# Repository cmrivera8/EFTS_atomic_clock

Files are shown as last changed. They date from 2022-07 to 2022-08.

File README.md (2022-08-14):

# EFTS_atomic_clock
The atomic clock described in this repository is used in the yearly European Frequency and Time Seminar (EFTS) hosted at ENSMM. This repository contains the original design files as well as the improved control software GUI in python (EFTS_atomic_clock/mac_control_program/qt_mac.py) and the microcontroller code (EFTS_atomic_clock/mac/mac.ino) embedded in the demonstrator.

When I started my contribution on this project, there were three atomic clocks, out of which only one was working correctly. The other two were marginally operational, with a weak absorption signal and low signal-to-noise ratio. This made it very difficult to lock the servo loops on the desired electronic transition. Moreover, the GUI was not intuitive and resulted in a not-ideal learning experience for the seminar attendees.

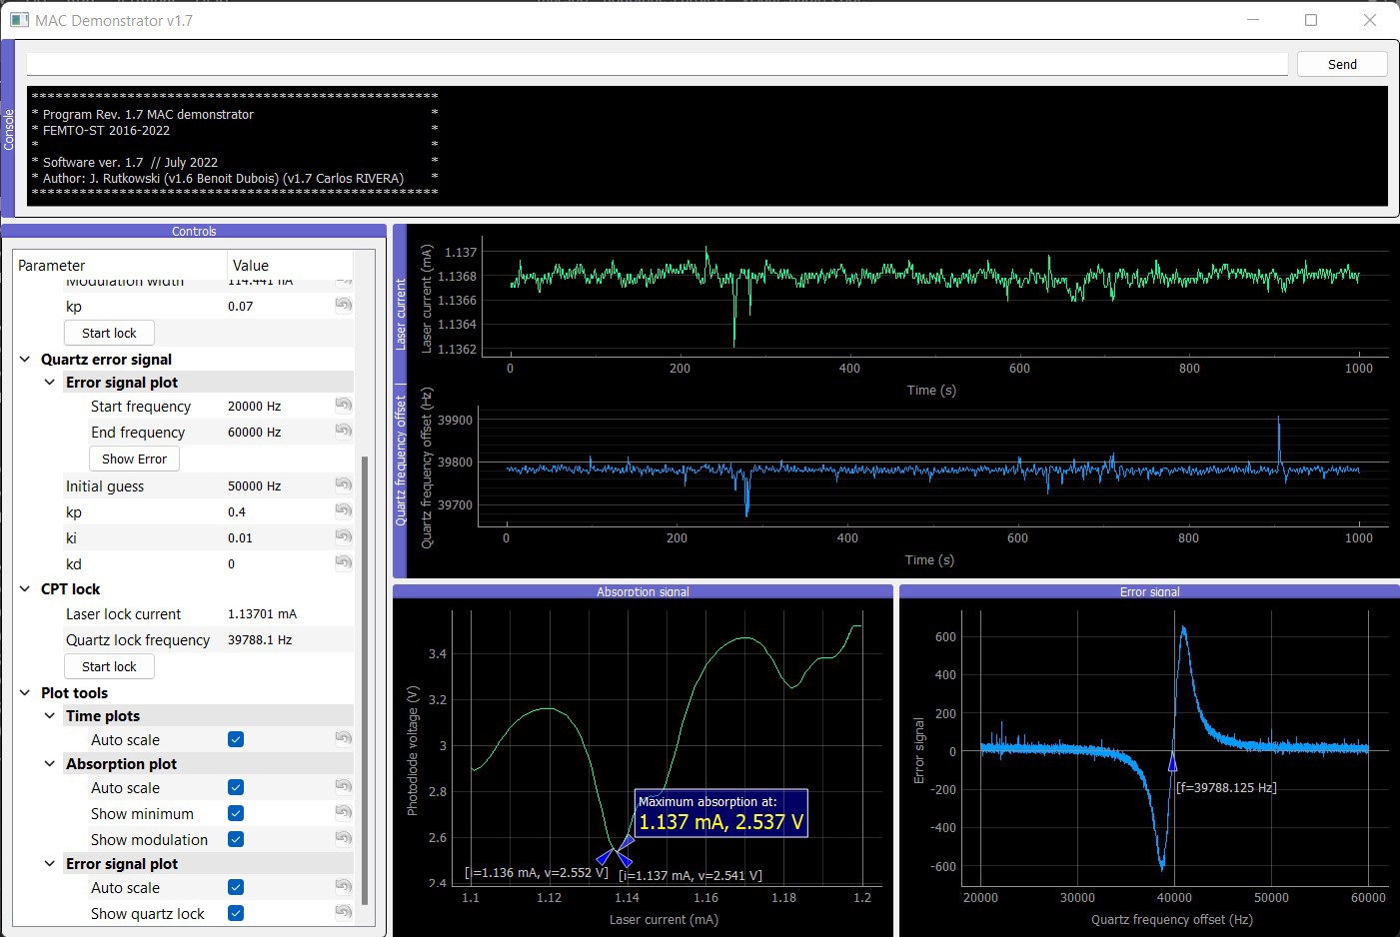
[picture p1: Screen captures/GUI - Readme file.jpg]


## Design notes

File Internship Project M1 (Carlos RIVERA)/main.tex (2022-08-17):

\documentclass[a4paper,12pt]{article}
\usepackage{geometry}
\geometry{a4paper} %paper format
\geometry{verbose,a4paper,tmargin=1.5cm,bmargin=2cm,lmargin=1.5cm,rmargin=1.5cm}  %margins

%\renewcommand{\thesection}{\Roman{section}}
%\renewcommand{\thesubsection}{\thesection.\Roman{subsection}}

\usepackage[english]{babel}
\usepackage{amsmath}
\usepackage{graphicx}
\usepackage{caption} %To use caption set up
\usepackage{subcaption}
\usepackage{wrapfig} %Wrap text to figure
\usepackage[export]{adjustbox} %Image aligment %Not compatible with \linespread
\usepackage{float}
\usepackage[singlespacing]{setspace}
\linespread{0.8}
\usepackage{hyperref}
\usepackage{titlesec}
\usepackage[T1]{fontenc}
%\usepackage{mathpazo} %Selecting font
\usepackage{microtype} %Improve justification
\usepackage{siunitx} %SI notation
%\usepackage[landscape]{geometry}
\usepackage{array}
\usepackage{color} %red, green, blue, yellow, cyan, magenta, black, white
\usepackage{bigdelim}
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
  morekeywords={scp,mkdir,rm,chmod,sudo,cp, apt, chown},              % Add keywords here
  commentstyle=\color{codegreen},
  keywordstyle=\bfseries\color{magenta},
  numberstyle=\tiny\color{codegray},
  stringstyle=\color{codepurple},
  breaklines=true,                % sets automatic line breaking
  tabsize=3,		              % sets default tabsize to 3 spaces
  frame=shadowbox,
  numbers=left,
  numberstyle=\scriptsize,
  prebreak=\usebox{\myprebreak},
  postbreak=\usebox{\mypostbreak},
  alsoletter=0123456789
}

\lstdefinestyle{c++}{
  language     = c++,
  basicstyle   = \footnotesize \ttfamily,
%   keywordstyle = [1]\color{keyword},
%   keywordstyle = [2]\color{STD},
%   keywordstyle = [3]\color{bits},
%   commentstyle = \color{comment},
%   stringstyle=\color{literals},
  morekeywords={self},              % Add keywords here
  commentstyle=\color{codegreen},
  keywordstyle=\color{magenta},
  numberstyle=\tiny\color{codegray},
  stringstyle=\color{codepurple},
  breaklines=true,                % sets automatic line breaking
  tabsize=3,		              % sets default tabsize to 3 spaces
  frame=shadowbox,
  numbers=left,
  numberstyle=\scriptsize,
  prebreak=\usebox{\myprebreak},
  postbreak=\usebox{\mypostbreak},
  alsoletter=0123456789
}
%

%Remove tab spaces
\newlength{\rawgobble}
\newlength{\gobble}
\newlength{\gobblea}
% The width of a single space. basicstyle from lstset should be used
\sbox0{\ttfamily \ }
% Remove a single space
\settowidth{\rawgobble}{\ttfamily \ }
\setlength{\rawgobble}{-\rawgobble}

\makeatletter
\def\sepstar#1*#2\relax{%
    \def\sepstarone{#1}%
    \def\sepstartwo{#2}%
}
\lst@Key{firstlineandnumber}\relax{\def\lst@firstline{#1\relax}\def\lst@firstnumber{#1\relax}}
\lst@Key{widthgobble}{0*0}{%
    % Reindent a bit by multiplying with 0.9, then multiply by tabsize and number of indentation levels
    \sepstar #1\relax
    \setlength{\gobble}{0.9\rawgobble}%
    \setlength{\gobble}{\sepstarone\gobble}%
    \setlength{\gobble}{\sepstartwo\gobble}%
    \setlength{\gobblea}{\gobble}%
    \addtolength{\gobblea}{10pt}%
    \def\lst@xleftmargin{\gobble}%
    \def\lst@framexleftmargin{\gobble}%
    \def\lst@numbersep{\gobblea}%
}
\makeatother
% Adding line number automatically
\makeatletter
\def\lst@MSkipToFirst{%
    \global\advance\lst@lineno\@ne
    \ifnum \lst@lineno=\lst@firstline
        \def\lst@next{\lst@LeaveMode \global\lst@newlines\z@
        \lst@OnceAtEOL \global\let\lst@OnceAtEOL\@empty
        \lst@InitLstNumber % Added to work with modified \lsthk@PreInit.
        \lsthk@InitVarsBOL
        \c@lstnumber=\numexpr-1+\lst@lineno % this enforces the displayed line numbers to always be the input line numbers
        \lst@BOLGobble}%
        \expandafter\lst@next
    \fi}
\makeatother
%
%Add extra level of sections
\usepackage{titlesec}
\usepackage{hyperref}

\titleclass{\subsubsubsection}{straight}[\subsection]

\newcounter{subsubsubsection}[subsubsection]
\renewcommand\thesubsubsubsection{\thesubsubsection.\arabic{subsubsubsection}}
\renewcommand\theparagraph{\thesubsubsubsection.\arabic{paragraph}} % optional; useful if paragraphs are to be numbered

\titleformat{\subsubsubsection}
  {\normalfont\normalsize\bfseries}{\thesubsubsubsection}{1em}{}
\titlespacing*{\subsubsubsection}
{0pt}{3.25ex plus 1ex minus .2ex}{1.5ex plus .2ex}

\makeatletter
\renewcommand\paragraph{\@startsection{paragraph}{5}{\z@}%
  {3.25ex \@plus1ex \@minus.2ex}%
  {-1em}%
  {\normalfont\normalsize\bfseries}}
\renewcommand\subparagraph{\@startsection{subparagraph}{6}{\parindent}%
  {3.25ex \@plus1ex \@minus .2ex}%
  {-1em}%
  {\normalfont\normalsize\bfseries}}
\def\toclevel@subsubsubsection{4}
\def\toclevel@paragraph{5}
\def\toclevel@paragraph{6}
\def\l@subsubsubsection{\@dottedtocline{4}{7em}{4em}}
\def\l@paragraph{\@dottedtocline{5}{10em}{5em}}
\def\l@subparagraph{\@dottedtocline{6}{14em}{6em}}
\makeatother

\setcounter{secnumdepth}{4}
\setcounter{tocdepth}{4}

% Add booktab table style:
\usepackage{booktabs}

\begin{document}

%% Title page
\begin{titlepage}

\newcommand{\HRule}{\rule{\linewidth}{0.5mm}}
\center 

\textsc{\LARGE Université Bourgogne Franche-Comté}\\[1.5cm] 
\textsc{\Large Internship Report Master 1}\\[0.5cm] 

\HRule \\[0.4cm]
{ \huge \bfseries Improvements on embedded systems used in the Time \& Frequencies Department}\\[0.4cm] %Improve title
\HRule \\[1.5cm]

\begin{figure}[!h]
\centering
\begin{subfigure}[b]{0.49\textwidth}
	\centering
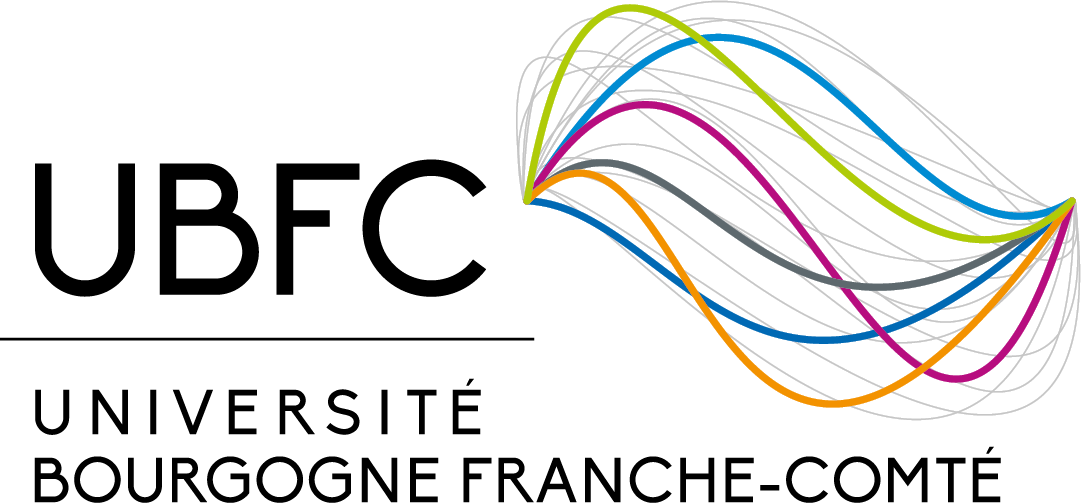
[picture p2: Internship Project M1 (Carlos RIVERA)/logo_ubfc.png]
	
	\captionsetup{justification=centering}
\end{subfigure}
\hfill
\begin{subfigure}[b]{0.49\textwidth}
	\centering
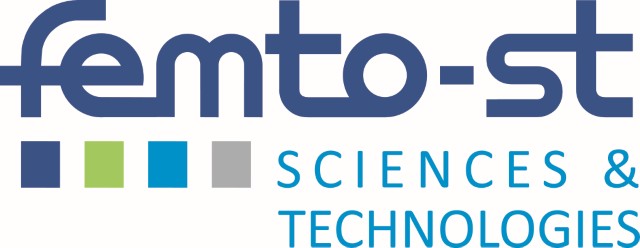
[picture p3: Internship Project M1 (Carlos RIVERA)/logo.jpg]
	
	\captionsetup{justification=centering}
\end{subfigure}
\end{figure}

\begin{center}
\vspace{2cm}
Presented by:\\ [0.4cm]
\begin{tabular}{ c    |    c } 
    Carlos RIVERA &  \normalsize \href{mailto:carlos_manuel.rivera_aguilar@edu.univ-fcomte.fr}{carlos\_manuel.rivera\_aguilar@edu.univ-fcomte.fr}
\end{tabular}
\end{center}
\vspace{2cm}
\begin{center}
Supervised by:\\ [0.4cm]
\begin{tabular}{ c    |    c } 
    Marion DELEHAYE &  \normalsize \href{mailto:marion.delehaye@femto-st.fr}{marion.delehaye@femto-st.fr} \\
    Rodolphe BOUDOT &  \normalsize \href{mailto:rodolphe.boudot@femto-st.fr}{rodolphe.boudot@femto-st.fr} \\
    Jean-Michel FRIEDT &  \normalsize \href{mailto:jeanmichel.friedt@femto-st.fr}{jeanmichel.friedt@femto-st.fr} \\
\end{tabular}
\end{center}
\vfill
{\large \today}\\[1cm] 
\vfill 

\end{titlepage}
  
%Table of contents and figures
\tableofcontents
\thispagestyle{empty}
\newpage
\listoffigures
\thispagestyle{empty}
\lstlistoflistings
\thispagestyle{empty}
\pagebreak

\setcounter{page}{1}

%Introduction:
\section{Introduction} 
The Time \& Frequencies department carries out investigations in applications and metrology of resonators and oscillators. The department is multifaceted with a focus on several scientific domains like electronics, hyperfrequency, acoustics, sciences and the shaping of crystalline materials, MEMS, photonics, signal processing, atomic physics, etc \cite{2022}.

The department’s research is conducted by three teams PiezoMEMS team, CoSyMA team (Composants et Systèmes Micro-Acoustiques) and OHMS team (Ondes, Horloges, Métrologie et Systèmes). The teams also work on common projects.

One of the domains on which OHMS team works is the creation of new frequency standard instruments (i.e. Atomic Clocks). The following technical report describes my collaboration with this department, specifically with OHMS team, as part of my internship for the Master 1 degree in Complex Systems, specialization: Smart Integrated Systems.

I worked on two separate projects; the first is "Superradiant laser instrumentation process", in which I improved the local network communication between the computers and the embedded system. The second project is "Improvements on CPT-based Cs microcell Atomic Clock pedagogical model" where I enhanced the performance and graphical user interface of the control software, and fixed two non-working atomic clocks (out of the existing three clocks).

%worked on 2 projects
%% First project
\section{Superradiant laser instrumentation process}
\subsection{Introduction}
The superradiant laboratory aims at generating an ultra-stable laser signal based on superradiant ytterbium atoms. Several lasers are used to achieve this. One of these lasers is at 399 nm (\mbox{751.3595 THz}) and it is used to excite the ytterbium atoms on an electronic transition that is 30 MHz wide. Hence, the laser frequency should be controlled within less than 30 MHz.

The laser frequency is measured within a few MHz using a Wavelength meter model WS8-2 manufactured by HighFinesse, that communicates, using UDP protocol, from a \textit{Windows computer} to a \textit{Red Pitaya} board (via Ethernet) to implement a PID control that regulates this frequency.

This communication process was dysfunctional, and it was not possible to re-use the UDP Server (\textit{Windows computer}) after the UDP Client (\textit{Red Pitaya}) was closed (and opened again to use a new setpoint frequency). It was necessary to open and close the UDP client twice to overcome this issue, which was very unreliable. A more robust protocol was intended, and I was able to modify both the Server and Client software to fix this problem.

Before the modifications took place, three computers were involved, hereafter referred to as:

\begin{itemize}
\itemsep 0em % To reduce space between items
    \item \textit{Windows computer:} this computer is running Windows 10 and had installed the wavelength meter software, UDP Server and the laser controller software. Since the first two do not require too much computational power and were malfunctioning when USB cameras used in the experiment were connected, a minimalistic single board computer, called \textit{LattePanda}, was later implemented (see section \ref{section:installation_lattepanda}).
    \item \textit{Artiq computer:} this computer is running Linux (Debian distribution) and is used to control the whole experiment via an Artiq\footnote{ARTIQ: Advanced Real-Time Infrastructure for Quantum physics is a control system for quantum information experiments, providing both hardware and software.} interface.
    \item \textit{Other computer:} located in another laboratory and running Linux, this computer contained the compilation toolchain for the \textit{Red Pitaya} board, as well as the UDP client software in charge of regulating the laser frequency, this computer was accessed and controlled remotely by the \textit{Artiq computer} via SSH\footnote{SSH: Secure Shell is a network communication protocol that enables two computers to communicate and share data.}.
\end{itemize}

% \subsection{Context} %Introduction and context are the same

Before I started my internship, the instrumentation scheme used to control the experiment's laser frequency is presented in figure \ref{fig:schematic}. A voltage controlled laser emits light and its frequency is then measured by a Wavelength meter. The instrument communicates the results to the \textit{Windows computer} via USB.

In the \textit{Windows computer}, the dedicated software of the instrument is installed. The results of the measurements are then streamed by a dedicated C++ program over Ethernet (UDP socket) to the \textit{Red Pitaya}.

The \textit{Red Pitaya} compares the measured value with a setpoint to generate an error signal that is then used to correct the laser frequency through a PID close loop controller.

The frequency setpoint is provided to the \textit{Red Pitaya} over Ethernet (SSH) by the \textit{Artiq computer} (Linux based), which allows having an interface with an option to modify the laser frequency and one to turn the laser lock on and off.

Another laboratory's computer (\textit{Other computer}, Linux based) was responsible to provide a NFS\footnote{NFS: Network File System is a networking protocol for distributed file sharing. A file system defines the way data in the form of files is stored and retrieved from storage devices, in our case from the computer to the \textit{Red Pitaya}.} directory to the \textit{Red Pitaya}. This allows to have real-time interaction with its content from the \textit{Artiq computer}. It also provides a cross-compilation toolchain, which is why multiple SSH processes were involved to modify the \textit{Red Pitaya} content (including the program written in C to voltage control the laser frequency).

\begin{figure}[!h]
    \centering
    
    \captionsetup{justification=centering}
    \caption{Laser frequency control instrumentation scheme at the beginning of the project.}
    \label{fig:schematic}
\end{figure}

For this project, the following objectives were set:
\begin{itemize}
\itemsep 0em % To reduce space between items
    \item To correct the fact that the cross compilation chain (oscimpDigital\footnote{oscimpDigital is an ecosystem designed to provide a consistent, chip independent, software/hardware cross-compile solution.} and Buildroot\footnote{Buildroot is a simple, efficient and easy-to-use tool to generate embedded Linux systems through cross-compilation.}) and the NFS directories were stored in \textit{Other laboratory's computer}, for which it was preferred to migrate them to the \textit{Artiq computer} (see section \ref{section:migration_section}).
    \item To have a standalone, single board computer running the Wavelength meter software and the C++ program, given that these two do not require a lot of computational power and that there are conflicts whenever a camera is connected via USB to the Windows Desktop computer (see section \ref{section:installation_windows10} and \ref{section:installation_lattepanda}).
    \item To fix the network communication software on the \textit{Red Pitaya} (written in C) and on the \textit{Windows computer} (written in C++), given that the communication between the two was not consistent, and it was necessary to close the socket twice whenever a new frequency setpoint was selected. Also, to implement a method that interrupts the communication process from the Artiq interface (see section \ref{subsec:udp_correction}).
    \item To have an automated start-up process to mount the NFS directory on the \textit{Red Pitaya} at power up, in case the latter had a power outage or just for a convenient everyday operation of the experiment (see section \ref{section:start_up_automation}).
\end{itemize}

\subsection{Migration of Red Pitaya environment between two computers}
\label{section:migration_section}

The migration process of the cross compilation chain (oscimpDigital and Buildroot) and the
NFS directory from the \textit{Other lab computer} to the \textit{Artiq computer} (as presented in figure \ref{fig:schematic}) is described in figure \ref{fig:migration_flowchart}.

\begin{figure}[!h]
    \centering
    
    \captionsetup{justification=centering}
    \caption{Migration process flowchart.}
    \label{fig:migration_flowchart}
\end{figure}

%Step 1:
\begin{step}
The folders "oscimpDigital" and "redpitaya" were copied from the \textit{Other computer} to the \textit{Artiq computer} using the "scp" command (listing \ref{lst:copy_osc_red}).

\begin{lstlisting}[style=bash,label={lst:copy_osc_red},caption={Copying files from the \textit{Other computer} to the \textit{Artiq computer}.}]
cd /home/manip/redpitaya/
scp -r pyb@172.16.120.154:~/oscimp/oscimpDigital ./oscimpDigital_pyb
scp -r pyb@172.16.120.154:~/oscimp/redpitaya ./redpitaya_pyb
\end{lstlisting}

\end{step}

%Step 2:
\begin{step}
It was necessary to download and install Buildroot in the \textit{Artiq computer}, it's imperative to download the new Buildroot files before the compilation instead of using the existing ones from the \textit{Other computer}, the latter contain hard links that are not compatible with the new location.

Running "make" using the old files may lead to unwanted results, such as the usage of the entire hard-disk. First the version "2019.05-rc3" was downloaded from \hyperlink{https://buildroot.org/downloads/buildroot-2019.05-rc3.tar.gz}{https://buildroot.org/downloads/buildroot-2019.05-rc3.tar.gz} and then extracted (listing \ref{lst:unpack_buildroot}), the name of the resulting folder was changed from "buildroot-2019.05-rc3" to "buildroot-2019.05-rc3\_redpitaya\_pyb".

\begin{lstlisting}[style=bash,label={lst:unpack_buildroot},caption={Extracting Buildroot.}]
tar -xf buildroot-2019.05-rc3.tar.gz
rm buildroot-2019.05-rc3.tar.gz
\end{lstlisting}

\end{step}

%Step 3:
\begin{step}
As per trabucayre's "redpitaya" GitHub repository \cite{trabucayre}, we must set up the "BR2\_EXTERNAL" variable to the location where the "redpitaya" directory is, as show in listing \ref{lst:br2_external}, to provide Buildroot based support for Red Pitaya (12, 14, and 16 bits) board.

\begin{lstlisting}[style=bash,label={lst:br2_external},caption={Setting the BR2\_EXTERNAL variable.}]
export BR2_EXTERNAL=~/redpitaya/redpitaya_pyb/
\end{lstlisting}

\end{step}

%Step 4:
\begin{step}
In order to match the previous installation, the board configuration file (options and features selected for the resulting OS) was copied into the \textit{Artiq computer} and then compiled with the "make" command, the commands of listing \ref{lst:copy_config} were performed in the directory "/home/manip/redpitaya/buildroot-2019.05-rc3\_redpitaya\_pyb/".

\begin{lstlisting}[style=bash,label={lst:copy_config},caption={Copying board ".config" file to the new Buildroot directory.}]
scp pyb@172.16.120.154:~/oscimp/redpitaya_buildroot/.config ./
make
\end{lstlisting}

In the middle of the compilation, there was an error fetching the file "linux-xilinx-v2019.1.tar.gz" from the internet, which is why it was copied from the \textit{Other computer} directly (listing \ref{lst:linux-xilinx}).

\begin{lstlisting}[style=bash,label={lst:linux-xilinx},caption={Copying xilinx file from previous installation.}]
scp pyb@172.16.120.154:~/oscimp/redpitaya_buildroot/dl/linux/linux-xilinx-v2019.1.tar.gz ./linux/linux-xilinx-v2019.1.tar.gz
make
\end{lstlisting}

\end{step}

%Step 5:
\begin{step}
Once the cross-compilation toolchain was installed, the next step was to set up the NFS directory in the \textit{Artiq computer}, following the instructions of oscimp's GitHub repository "oscimpDigital" \cite{oscimp}, the designated location was "/home/manip/redpitaya/oscimpDigital\_pyb/nfs" (listing \ref{lst:mkdir_nfs}).

\begin{lstlisting}[style=bash,label={lst:mkdir_nfs},caption={Creating NFS directory.}]
mkdir /home/manip/redpitaya/oscimpDigital_pyb/nfs
\end{lstlisting}

Inside the directory "/home/manip/redpitaya/oscimpDigital\_pyb/" the "settings.sh" file was found, which contains all environment variable information required for the compilation of the library, drivers and modules, as shown in listing \ref{lst:nfs_settings}, only the "BR\_DIR" and "OSCIMP\_DIGITAL\_NFS" variables needed to be updated.

\begin{lstlisting}[style=bash,label={lst:nfs_settings},caption={Updating variables "settings.sh" file.}]
export BR_DIR='/home/manip/redpitaya/buildroot-2019.05-rc3_redpitaya_pyb'
export OSCIMP_DIGITAL_NFS='/home/manip/redpitaya/oscimpDigital_pyb/nfs'
\end{lstlisting}

\end{step}

%Step 6:
\begin{step}
The libraries (listing \ref{lst:libraries}), drivers (listing \ref{lst:drivers}) and modules (listing \ref{lst:modules}) must be compiled; however, for the latter, the Makefile fails at copying the file "module\_generator" to the "/usr/local/bin" directory, thus, this was done manually with the \textbf{sudo} command (listing \ref{lst:modules}, line 5).

\begin{lstlisting}[style=bash,label={lst:libraries},caption={Compiling the libraries.}]
cd /home/manip/redpitaya/oscimpDigital_pyb/lib
make install_ssh
\end{lstlisting}

\begin{lstlisting}[style=bash,label={lst:drivers},caption={Installing the drivers.}]
export PATH=~/redpitaya/buildroot-2019.05-rc3_redpitaya_pyb/output/host/usr/bin/:$PATH
cd /home/manip/redpitaya/oscimpDigital_pyb/linux_driver
make install_nfsdir
\end{lstlisting}

\begin{lstlisting}[style=bash,label={lst:modules},caption={Compiling the module generator tool.}]
cd /home/manip/redpitaya/oscimpDigital_pyb/app/tools/module_generator
chmod +x Makefile
make install

sudo cp module_generator /usr/local/bin
\end{lstlisting}

\end{step}

\begin{step}
To finish the configuration on the new host (\textit{Artiq computer}), the "nfs-kernel-server" must be installed and the rights of the nfs directory changed, which allowed to have access to bistreams, applications and drivers through the NFS shared directory, this is accomplished by running the commands in listing \ref{lst:nfs_kernel}. 

\begin{lstlisting}[style=bash,label={lst:nfs_kernel},caption={Installing nfs-kernel server and changing directory rigths.}]
apt install nfs-kernel-server nfs-common

cd /home/manip/redpitaya/oscimpDigital_pyb/nfs
chown -R $(id -u).$(id -g) .
\end{lstlisting}

\end{step}

\begin{step}
The last step of the migration process was to compile and test the project (UDP Client on Red Pitaya), for which the project files were copied from the \textit{Other computer} and then compiled (listing \ref{lst:compile_test_1}).

%Check if this is the correct location line 3 and 4
\begin{lstlisting}[style=bash,label={lst:compile_test_1},caption={Copying project files and compile.}]
cd ~/redpitaya/oscimpDigital_pyb/projects/
scp -r pyb@172.16.120.154:~/oscimp/projects ~/redpitaya/oscimpDigital_pyb/projects/
make && make install

cd ~/redpitaya/oscimpDigital_pyb/nfs/redpitaya/laser_lock_LSR/bin/
scp -r pyb@172.16.120.154:~/oscimp/nfs/redpitaya/laser_lock_LSR/bin/start_lock.sh ./
scp -r pyb@172.16.120.154:~/oscimp/nfs/redpitaya/laser_lock_LSR/bin/laser_lock_LSR_us.sh ./
\end{lstlisting}

Running the software gave a segmentation fault error, upon close examination, it was not able to create and access a file in the current directory due to missing rights (fixed in listing \ref{lst:compile_test_2} line 1), there was also a missing file on the project's bitstreams directory (fixed in listing \ref{lst:compile_test_2} line 3 to 4).

\begin{lstlisting}[style=bash,label={lst:compile_test_2},caption={Correcting directory rights and copying missing file on bitstreams.}]
chmod -R 777 ~/redpitaya/oscimpDigital_pyb/nfs/redpitaya

cd ~/redpitaya/oscimpDigital_pyb/projects/laser_lock_LSR/design
cp laser_lock_LSR_wrapper.bit.bin ~/redpitaya/oscimpDigital_pyb/nfs/redpitaya/laser_lock_LSR/bitstreams/
\end{lstlisting}

\textbf{Conclusion:} Finally, the Red Pitaya software was tested successfully and there is no longer a dependency on the \textit{Other computer}. The new instrumentation scheme, as shown in figure \ref{fig:schematic_2}, requires only two computers located in the experiment's laboratory.

\begin{figure}[!h]
    \centering
    
    \captionsetup{justification=centering}
    \caption{Laser frequency control instrumentation scheme after migration.}
    \label{fig:schematic_2}
\end{figure}

\end{step}

\subsection{Installation of Windows 10 on Raspberry Pi}
\label{section:installation_windows10}
%introduction: we had an issue because there are some error when we want to use the wavelength meter software together with a camera on windows computer#1. This is because of the wavelength meter (the manufacturer admitted it). We decided to move the wavelength meter to a minimalistic computer.
While trying to use simultaneously the wavelength meter and some USB camera, we had multiple crashes on the Windows computer. It turns out that the wavelength meter software is defective and is not compatible with the use of some cameras simultaneously. We decided to install the wavelength meter software on a different computer. In a first instance, the option to have the Wavelength meter software on a single board Raspberry Pi computer was explored, for which there were two options:

\begin{itemize}
\itemsep 0em % To reduce space between items
\item To install a precompiled Raspbian OS\footnote{OS: Operating System} and emulate a Windows environment (using Wine\footnote{Wine is a free and open-source compatibility layer that aims to allow application software and computer games developed for Microsoft Windows to run on Unix-like operating systems.}) in order to install and run the software. In case of success, to tailor an optimized Linux operating system with Buildroot.
\item To install a ARM Windows 10 OS.
\end{itemize}

\subsubsection{Installation of Raspbian OS and Wine32 on the Raspberry Pi}

One of the main challenges for this approach is the fact that the Raspberry Pi ARM-based processor is fundamentally different from the x86-based CPU found in a typical PC. It was necessary to install box86 to emulate a x86 system on the Raspberry Pi and then Wine 32 to run Windows applications. However, incompatibility issues were found.\\

Despite of the fact that it was possible to install the software with wine32, it was not possible to obtain a correct behavior from the GUI of the software, it presented black sections and it was unresponsive as show in figure \ref{fig:raspbian}. 

\begin{figure}[!h]
    \centering
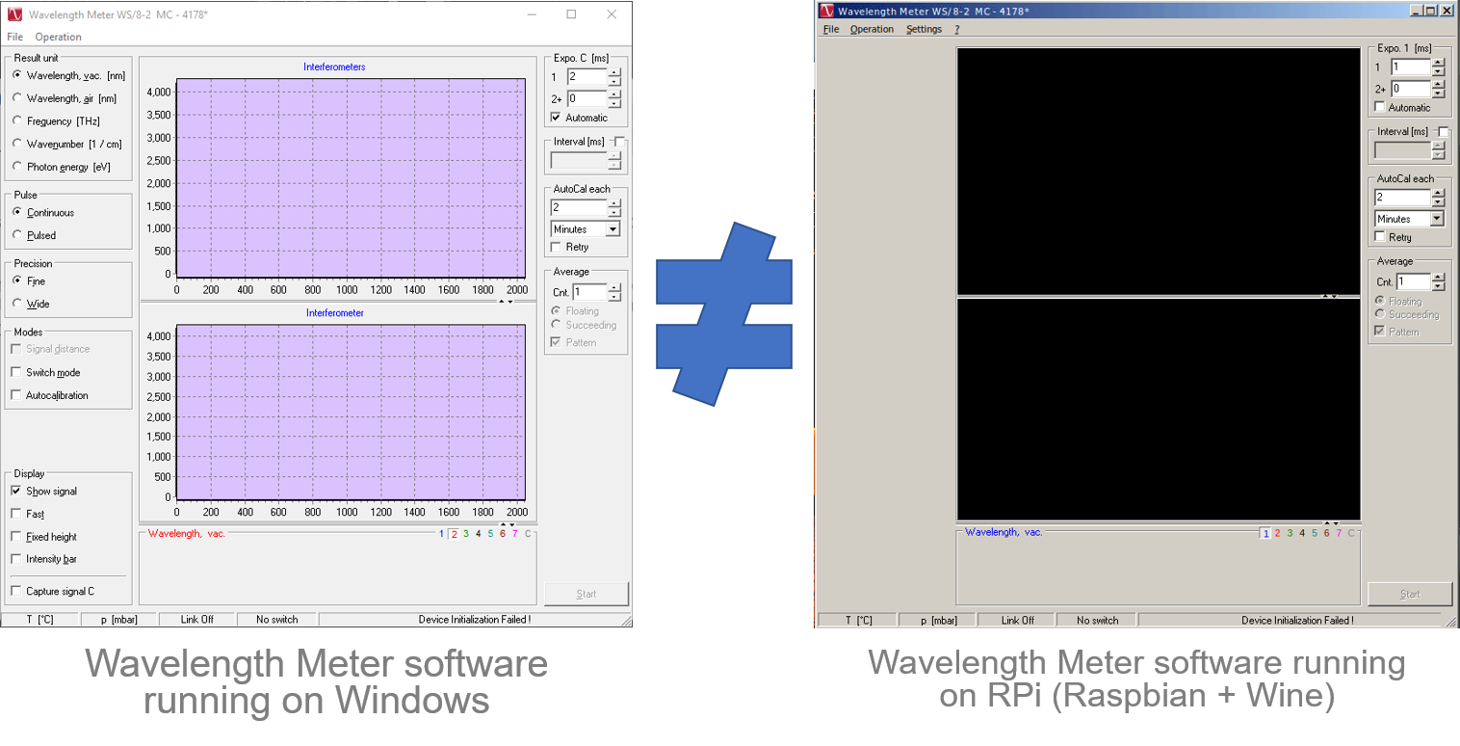
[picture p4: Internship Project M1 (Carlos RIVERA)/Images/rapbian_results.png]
    
    \captionsetup{justification=centering}
    \caption{Results of installing the wavelength meter software on Raspbian.}
    \label{fig:raspbian}
\end{figure}

\subsubsection{Installation of ARM Windows 10 OS on the Raspberry Pi}

Since it was not possible to run the Wavelength meter software on Raspbian due to their architectures incompatibility, the next option was to install a Windows 10 ARM version, which is compatible with the Raspberry Pi 4 and allows to run native Windows applications, it developed by the WoR (Windows on Raspberry Pi) project.

There is no legal way to download ISO files for Windows 10 ARM. Instead, a legal UUP dump file was downloaded, or "Unified Update Platform". This is a way for Microsoft to share its latest advances within its "Insider Preview" program. In short, the process was to download the UUP file, build a full ISO image from that file on the computer, then flash that ISO to boot on the Raspberry Pi.

With this approach it was possible to install the software on the Raspberry Pi. However, at initialization the device was not found (figure \ref{fig:device_not_found}), even though at installation a driver was installed. This appears to be an issue with the operating system which doesn't provide yet full support for peripherals such as USB ports. 

\begin{figure}[!h]
    \centering
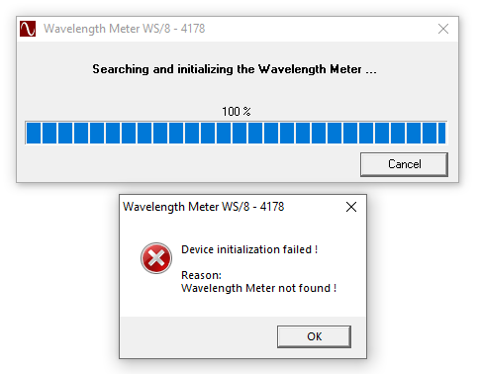
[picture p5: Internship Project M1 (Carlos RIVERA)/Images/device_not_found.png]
    
    \captionsetup{justification=centering}
    \caption{ARM Windows on RPi error: Wavelenth Meter not found.}
    \label{fig:device_not_found}
\end{figure}

\textbf{Conclusion:} The Raspberry Pi with ARM Windows was not robust enough to accommodate the software and be reliable in a daily basis operation, due to its slow speed and being prone to freeze or reset.

\subsection{Installation of Wavelength meter on Latte Panda single board computer}
\label{section:installation_lattepanda}

Finally, it was decided to install the Wavelength meter software on a Latte Panda single board computer (figure \ref{fig:latte_panda}) with the specifications described in table \ref{table:latte_panda_specs}.

\renewcommand{\arraystretch}{1.1}

\begin{table}[!h]
\begin{tabular}{ | l | l | }
\hline
\textbf{Processor}          & Intel Cherry Trail Z8350 Quad Core, 2M Cache, up to 1.92 GHz  \\ \hline
\textbf{Operating system}   & Pre-installed Windows 10                                      \\ \hline
\textbf{Ram}                & 4GB DDR3L                                                     \\ \hline
\textbf{Storage Capability} & 64GB                                                          \\ \hline
\textbf{GPU}                & Intel HD Graphics, 12 EUs @200-500 Mhz, single-channel memory \\ \hline
\textbf{Connectivity}       & WiFi and Bluetooth 4.0                                        \\ \hline
\textbf{Peripherals}        & One USB 3.0 port and two USB 2.0 ports                         \\ \hline
\textbf{Dimension of board} & 88 mm * 70 mm                                                    \\ \hline
\end{tabular}
\caption{Specifications of LattePanda 4G/64G.}
\label{table:latte_panda_specs}
\end{table}

\begin{figure}[!h]
    \centering
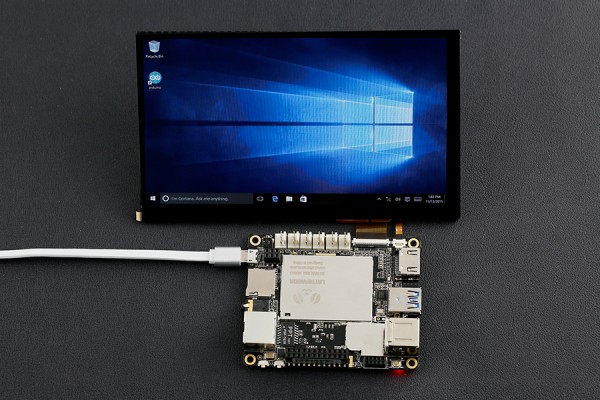
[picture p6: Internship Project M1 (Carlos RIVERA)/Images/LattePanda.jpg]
    
    \captionsetup{justification=centering}
    \caption{LattePanda single board computer running a full version of Windows 10.}
    \label{fig:latte_panda}
\end{figure}

\textbf{Conclusion:} The installation was flawless for both the Wavelength meter software as well as the UDP Server. After testing, it was possible to establish a connection from the LattePanda UDP Server to the Red Pitaya UDP Client, thus control the laser frequency from the Artiq interface. The resulting instrumentation scheme is presented in figure \ref{fig:schematic_3}.
%old: when the UDP socket must be closed by the Red Pitaya (see section \ref{subsec:udp_correction})

%Add screenshots/photos of the software working on the LattePanda.
% \textcolor{red}{Photos pending}

\begin{figure}[!h]
    \centering
    
    \captionsetup{justification=centering}
    \caption{Laser frequency control instrumentation scheme after the addition of LattePanda.}
    \label{fig:schematic_3}
\end{figure}

\newpage
\subsection{Correction of network communication between Red Pitaya and Wavelength meter}
\label{subsec:udp_correction}

The frequency measured by the wavelength meter is sent to the \textit{Red Pitaya} so that it can generate an error signal. Since the wavelength meter software comes with C++ libraries, it was chosen to use a UDP protocol to exchange information between the \textit{Windows computer} (running the wavelength meter software) and the \textit{Red Pitaya}.

An UDP datagram-based protocol was implemented before I started the internship. However this process was erratic and required the client socket (Red Pitaya) to be closed twice every time a new setpoint was selected. To circumvent this problem, a series of scripts were created and run from the \textit{Artiq computer} (SSH control of the Red Pitaya) but it was intended to have a robust and reliable network communication for the experiment that would also allow future enhancements to the instrumentation scheme.

\textit{Normally in the UDP protocol, the client does not form a connection with the server like in TCP and instead just sends a datagram to request for data. Similarly, the server doesn't need to accept a connection and just waits for datagrams request to arrive} \cite{geeksforgeeks_2022}, as show in figure \ref{fig:server-and-client}. However, upon closer inspection of the server and client code, the flowchart of figure \ref{fig:udp_before} was deduced.

\begin{figure}[!h]
    \centering
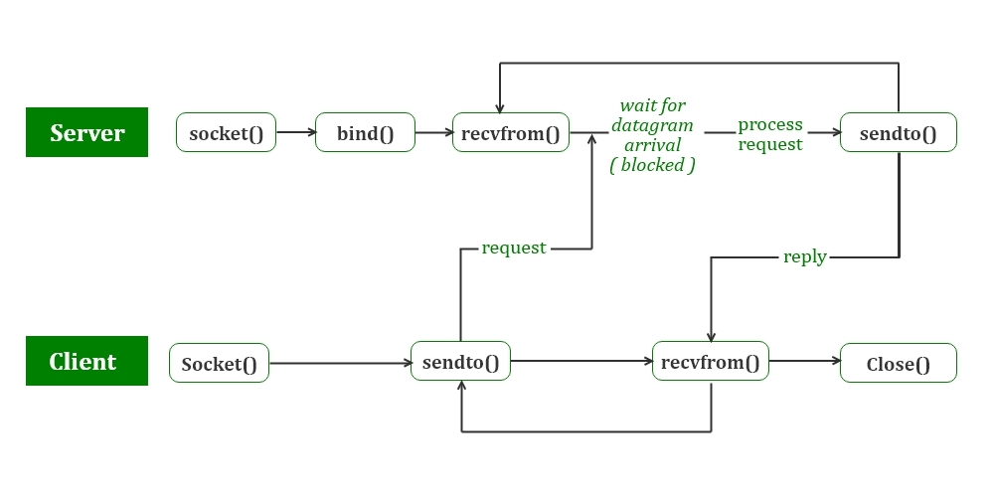
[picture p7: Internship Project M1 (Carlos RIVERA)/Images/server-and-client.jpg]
    
    \captionsetup{justification=centering}
    \caption{Standard UDP protocol \cite{geeksforgeeks_2022}}
    \label{fig:server-and-client}
\end{figure}

\begin{figure}[!h]
    \centering
    
    \captionsetup{justification=centering}
    \caption{Implemented UDP protocol before improvements.}
    \label{fig:udp_before}
\end{figure}

\newpage
There was a miscommunication between the Client and the Server, in which the former was not able to send the "close signal" in order to terminate the process (i.e to establish a new setpoint and start again). The solution implemented is shown in figure \ref{fig:udp_after}.

\begin{figure}[!h]
    \centering
    
    \captionsetup{justification=centering}
    \caption{Implemented UDP protocol after improvements.}
    \label{fig:udp_after}
\end{figure}

First for the Server code (listing \ref{lst:server_close}), a "while" loop was introduced (line 101) to ensure that every time a "close signal" is received, the socket is closed and a new one is created and bound to the port. Thus, every time the Server sends information to the Client, it also verifies if the latter has replied back with the word "Bye" (line 227 to 230), if that is the case, the code "breaks" out of the first loop (line 229) and then out of the main loop (line 235), effectively restarting the process by closing the socket (line 237) and continuing from the start again (line 106).

\pagebreak
\lstinputlisting[nolol=true,label={lst:server_close},caption={Key elements of the improved Server code (not complete code).},style=c++,widthgobble=1*3,linerange={101-101,106-109,116-127,142-150,153-157,171-171,184-184,196-197,220-220,227-231,234-242}]{Code/windows software.cpp} \vspace{0.4cm}

Then for the Client, as exhibited in listings \ref{lst:client_close} and  \ref{lst:client_close2}, the method used to close the socket in real time (and avoid interrupting the data exchange that locks the laser frequency), was to have a file named "stop\_pid" in the Red Pitaya, which by default contains a "0" (line 181 to 189), that is read after every cycle of the main "while" loop (line 285 to 293). When the content of the file is set to "1" by the Artiq program, the socket is closed and the "while" loop quits (line 291 and 292 respectively). 
\lstinputlisting[nolol=true,label={lst:client_close},caption={Client code, creation of "stop\_pid" file.},style=c++,widthgobble=1*3,linerange={181-189}]{Code/laser_lock_LSR.c} \vspace{0.4cm}

\lstinputlisting[nolol=true,label={lst:client_close2},caption={Client code, checking the "stop\_pid" file to close the socket.},style=c++,widthgobble=2*3,linerange={285-293}]{Code/laser_lock_LSR.c} \vspace{0.4cm}

As previously mentioned and presented in figure \ref{fig:udp_before}, the Client must send a "close signal" to the Server in order to restart the socket, this is performed inside the "close\_udp()" function, as shown in listing \ref{lst:close_udp}, the word "Bye" is sent using the "sendto" (line 111) function and then the Client socket itself is closed (line 112).

\lstinputlisting[nolol=true,label={lst:close_udp},caption={Client side "close\_udp" function.},style=c++,widthgobble=0*3,linerange={108-113}]{Code/laser_lock_LSR.c} \vspace{0.4cm}

% \subsection{Improvement of UDP socket closing method} %This section is explained in the previous one.

\subsection{Automation of NFS mounting and program execution at startup of Red Pitaya}
\label{section:start_up_automation}

In order to automate the NFS directory mounting and the program execution at startup, multiple approaches were considered and tested. However, the most reliable was do add a bash script in the system directory "/etc/network/if-up.d/", all the scripts stored there are executed once the network connection is established.

\pagebreak
\begin{lstlisting}[style=bash,label={lst:startup},caption={Automated NFS mounting and program execution script.}]
#!/bin/sh

echo ">>Mounting /opt/" > /dev/kmsg
sleep 5
mount /opt/

node_process_id=$(pidof laser_lock_LSR_us)
if [[ -z $node_process_id ]]; then
echo "$SERVICE stopped"
echo ">>Running laser lock" > /dev/kmsg
cd /opt/redpitaya/laser_lock_LSR/bin
./laser_lock_LSR_us.sh
./start_lock.sh &
fi
\end{lstlisting}

The implemented bash script is shown in listing \ref{lst:startup}, first the "\/opt" directory is mounted after a 5 seconds delay (line 3 to 5), then the "laser lock" program is executed in case it was not running (line 7 to 14). It's worth pointing out that the ampersand symbol added to the execution of the program in line 13 is critical, given that the program must run in the background.

\subsection{Partial conclusion}

After these improvements, the laser frequency lock for the blue laser is more robust, hands-free, and the wavelength meter can be operated from the \textit{LattePanda} without affecting the cameras of the experiment.

%% Second project
\newpage
\section{Improvements on CPT-based Cs microcell Atomic Clock pedagogical model}
\subsection{Introduction}
\label{section:tp_info}
The atomic clock described in this section is used in the yearly European Frequency and Time Seminar (EFTS) hosted at ENSMM\footnote{ENSMM: École Nationale Supérieure de Mécanique et des Microtechniques.}, \textit{which is a no-profit intensive full-week seminar intended to provide education and training with lectures and lab sessions to a broad audience: Engineers, Ph.D. students, post-docs, young scientists, newcomers, etc. }\cite{efts}

The following section has been extracted from the practical work document \cite{tp}. Figure \ref{fig:globalcpt} shows the architecture of a miniature Cs cell atomic clock based on coherent population trapping (CPT).

\begin{figure}[h!]
	\centering
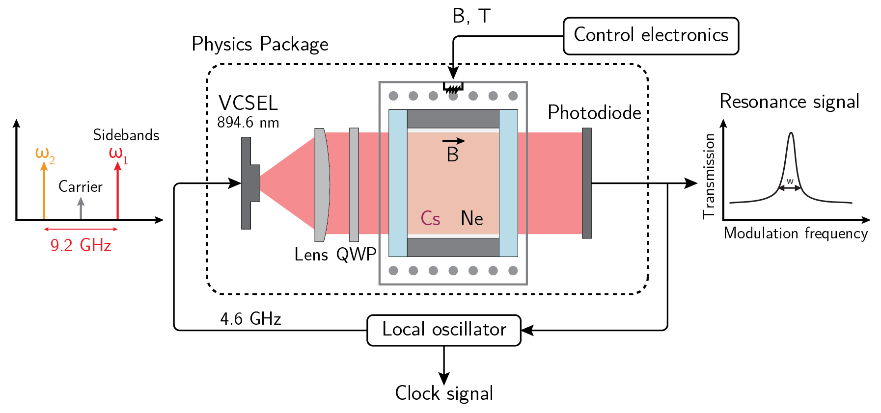
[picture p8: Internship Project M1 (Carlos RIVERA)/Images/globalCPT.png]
	
	\caption{Simplified architecture of a buffer-gas filled Cs microcell CPT atomic clock.}
	\label{fig:globalcpt}
\end{figure}

Cs vapor is filled in a glass-silicon-glass micro-fabricated cell whose technology is described in~\cite{hasegawa}. The Cs cell is filled with a pressure buffer gas. The buffer gas slows down atoms in the microcell and increases the time for the atoms to reach the cell walls. It also reduces the first-order Doppler effect and leads to operation in the Lamb-Dicke regime~\cite{dicke}. Eventually, it helps to detect narrow CPT resonances.

Atoms in the cell interact with a dual-frequency (in the ideal case) optical field generated by a VCSEL laser whose injection current is directly modulated at 4.596 GHz through a bias-tee. This generates two first-order optical sidebands separated by about 9.192 GHz, required to produce the CPT interaction. The laser output beam crosses a neutral density filter to attenuate the optical power and a quarter-wave plate to polarize circularly the optical beam. The light transmitted through the cell is detected by a photodiode.

When the frequency difference between both first-order optical sidebands exactly equals the Cs ground-state hyperfine splitting (9.192 631 770 GHz), atoms are trapped through a quantum interference process in a quantum superposition of both ground states (see Fig.~\ref{fig:ppeCPT}). In this so-called dark state, the light atomic absorption is reduced and the atomic vapor transparency is increased. The CPT resonance linewidth is ultimately limited by the microwave CPT coherence relaxation time and can be measured to be of about 1 kHz in a buffer-gas filled micro-fabricated cell. The signal at the output of the photodiode is used in two main servo loops. The first one is dedicated to the stabilization of the laser frequency onto the bottom of a homogeneously broadened optical line. The second loop stabilizes the local oscillator (LO) frequency onto the atomic clock transition.

\begin{figure}[h!]
	\centering
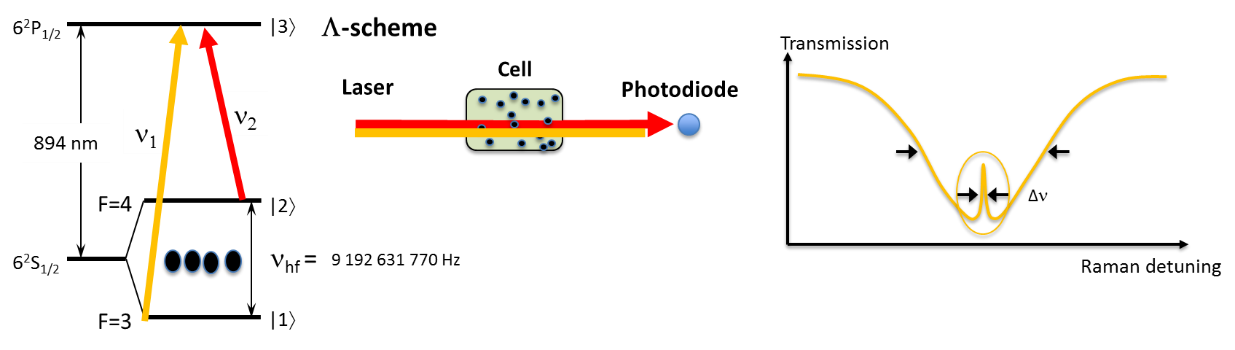
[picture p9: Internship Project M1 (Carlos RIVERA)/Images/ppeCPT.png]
	
	\caption{Basic principle of CPT.}
	\label{fig:ppeCPT}
\end{figure}

\newpage
\subsubsection{Laser servo loop}

% \newsavebox{\laserAnimation}
% \sbox{\laserAnimation}{\animategraphics[width=0.5\textwidth,autoplay,loop]{2}{animation_laser_servo_loop/laser1_}{0}{36}}

% \newsavebox{\quartzAnimation}
% \sbox{\quartzAnimation}{\animategraphics[controls={play,step},width=0.5\textwidth,autoplay,loop]{2}{animation_quartz_servo_loop/quartz_}{0}{61}}

The purpose of the laser servo loop is to set and lock the laser current (i.e. laser frequency) in the bottom of the absorption profile where the CPT signal is located. As shown in figure \ref{fig:laser_servo_loop}, the laser current is shift to the right and left by a fixed modulation width and the photodiode measurements are recorded in two variables ("val1" and "val2"). The error signal is then calculated as the difference between "val1" and "val2".

\begin{figure}[!h]
\centering
\begin{subfigure}[c]{0.49\textwidth}
	\centering
	\animategraphics[controls={play,step},width=\textwidth,autoplay,loop]{2}{animation_laser_servo_loop/laser1_}{0}{50}
	\captionsetup{justification=centering}
\end{subfigure}
\hfill
\begin{subfigure}[c]{0.49\textwidth}
	\centering
	
	\captionsetup{justification=centering}
\end{subfigure}
 \caption{Laser servo loop.}
\label{fig:laser_servo_loop}
\end{figure}

The calculated error signal can be used to adjust the laser current to an equilibrium point between the two modulation values ("val1" and "val2"). To determine the new laser current, the error signal is multiplied by a gain "Kp" and the process is repeated until the user decides to stop the servo loop. 

By adjusting the values of the modulation width and the gain "Kp", it is possible to obtain a fast response with a deterioration in the stability of the loop, or vice-versa, a slow and steady response.

\subsubsection{Quartz servo loop}

Similar to the laser servo loop, the quartz servo loop relies on setting an initial frequency and then modulate it to calculate an error signal (we want the error signal to be equal to 0). As shown in figure \ref{fig:quartz_servo_loop}, the process to lock the quartz frequency is to first set the initial PLL frequency by applying a voltage to the VCO\footnote{VCO: Voltage Controlled Oscillator.} of the 10 Mhz quartz oscillator (which is the reference for the PLL). Next, using the PLL synthesizer and its frequency-shift keying capability (when the logical value of pin 12 "TXDATA" changes), the central carrier frequency of the PLL is shifted by 1 kHz to the right in the frequency domain (i.e. the frequency is increased by 1 kHz).

The photodiode measurements before and after the modulation are recorded and are used to calculate the error signals. These error signals are used with a PID controller to lock the PLL frequency to an equilibrium point.

\begin{figure}[!h]
\centering
\begin{subfigure}[c]{0.49\textwidth}
	\centering
	\animategraphics[controls={play,step},width=\textwidth,autoplay,loop]{2}{animation_quartz_servo_loop/quartz_}{0}{61}
	\captionsetup{justification=centering}
\end{subfigure}
\hfill
\begin{subfigure}[c]{0.49\textwidth}
	\centering
	
	\captionsetup{justification=centering}
\end{subfigure}
 \caption{Quartz servo loop.}
\label{fig:quartz_servo_loop}
\end{figure}

The reason why the equilibrium point is found around half of the transmission peak height and not at its maximum value, is due to the fact that the values compared are the ongoing PLL frequency and the 1 kHz right shifted PLL frequency. When both frequencies produce the same output in the photodiode, the error signal is 0 and the locked frequency is found at the ongoing PLL frequency, i.e. to the left of the transmission peak, this is demonstrated in figure \ref{fig:transmission_peak}.

\begin{figure}[h!]
	\centering
	
	\caption{Locked frequency at half of the transmission peak height.}
	\label{fig:transmission_peak}
\end{figure}

% \vfill
\newpage
\subsection{Context}
When I started my contribution to this project, there were three atomic clocks, out of which only one was working perfectly (hereafter referred to as \textit{Clock 1}). The other two were marginally operational, with a weak absorption signal and low signal-to-noise ratio. This made it very difficult to lock the servo loops on the desired electronic transition. Moreover, the GUI\footnote{GUI: Graphical User Interface, is a series of visual components that allow the interaction between the user and the program.} used (see figure \ref{fig:gui_v1.6}) was not intuitive.

The project had plenty of room for improvement, due to  the following reasons:

\begin{itemize}
\itemsep 0em % To reduce space between items
    %Controls
    \item The control of the demonstrator relied on non-intuitive commands typed in the software's console, for example, typing \texttt{"t 30000 s"} to generate a ramp that started from the laser current equal to "30000" \textit{machine units}\footnote{Machine units, are positive integer values from 0 to $2^{16}$ that are used by the code but have no evident relation with real physical units.}, (see section \ref{section:replacement_serial}).
    \item All the units used in the program were \textit{machine units} instead of real physical units such as volts, amperes and Hertz. This was very counterproductive pedagogically speaking, (see section \ref{section:physical_units}).
    \item A panel named "Control" was present but some of their elements were not operational (e.g. laser temperature control) and others were not relevant for the operation of the demonstrator (such as the Synthesizer control elements, since the synthesizer is controlled internally for every function), (see section \ref{section:replacement_serial}).
    \item It was not possible to change the quartz oscillator scan parameters (initial and final scan values), (see section \ref{section:scan_params}).
    %Main operation
    \item It was necessary to press a physical button outside the demonstrator to stop a never-ending loop process, i.e "Laser scan" or "Laser lock", (see section \ref{section:stop_process}).
    \item An oscilloscope had to be connected at all times to the demonstrator in order to monitor the output of the photodiode, (see section \ref{section:output_monitoring}).
    %Graphical
    \item The graphs were missing titles and axis labels, (see section \ref{section:graphs}).
    \item Since the demonstrator worked only with \textit{machine units} and with the oscilloscope measurements, it was difficult to identify the laser current value for maximum absorption, (see section \ref{section:max_absorb}).
    \item It was difficult to identify when the servo loops got locked or unlocked.
    % \item It was not intuitive when the servo loops were locked, only the time plots were available. %Covered in previous item
    \item When doing a quartz scan\slash modulation, it was only possible to visualize the "error signal" but not the CPT signal itself, (see section \ref{section:CPT}).
    %Others
    
\end{itemize}

\begin{figure}[!h]
    \centering
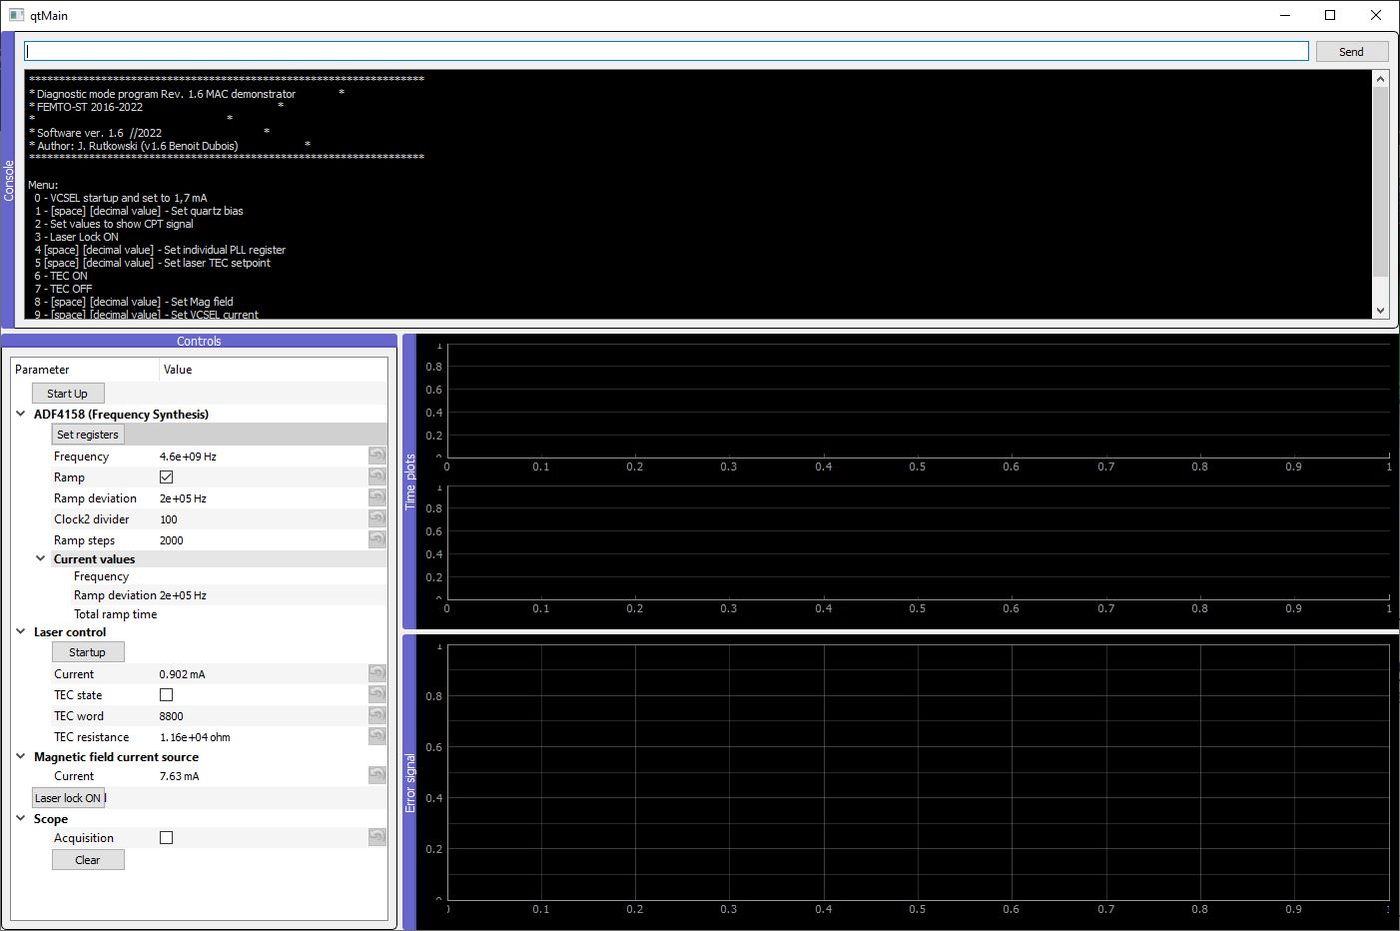
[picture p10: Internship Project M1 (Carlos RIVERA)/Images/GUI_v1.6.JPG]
    
    \captionsetup{justification=centering}
    \caption{Micro Atomic Clock demonstrator program before improvements, version 1.6.} 
    \label{fig:gui_v1.6}
\end{figure}

While working on this project I was able to modify both the Python based GUI and the Arduino based microcontroller code to overcome these problems, in order to have a more reliable, intuitive, easy to use and robust atomic clock demonstrator. Furthermore, I fixed two of the non-operational atomic clocks (see section \ref{section:repair_atomic_clocks}).

The improvements added in the context of this year's EFTS, were well received and appreciated by my supervisors and the participants to the seminar, to the point of being honored by the event's chair, Dr. Enrico Rubiola, with a recognition diploma for my contribution.
\pagebreak

\subsection{Physical components}

\begin{figure}[!h]
    \centering
    
    \captionsetup{justification=centering}
    \caption{Components of the atomic clock demonstrator.} 
    \label{fig:mac_components}
\end{figure}

The atomic clock demonstrator (see figure \ref{fig:mac_components}) consist of the following components:

\begin{enumerate}[wide, labelwidth=!, labelindent=0pt]
	\item \textbf{AC power connector.}
	\item \textbf{Power supply: } Converts the 240 VAC from mains voltage to 12 VDC.
	\item \textbf{Voltage regulator: } Steps down the 12 VDC coming from the power supply to 5 V and 3.3 V. 
	\item \textbf{Arduino Due and shield connector: } Main processing unit to control of the system, its content can be programmed with the same USB port used to operate the clock; the shield provides a connector for the "Atomic clock board".
	\item \textbf{Physical package: } This includes the VCSEL, photodiode (with a current to voltage circuit), heating element for the vapor cell and the coil to provide a static magnetic field. The terminals allow a convenient way to unmount it from the main board. The coaxial RF jack, connects to a Bias-Tee that mixes the laser current with the microwave signal coming from the synthesizer.
    \item \textbf{Cell temperature controller: } This circuit contains an Atmega 32u4 microcontroller to implement a PID controller, a power stage to drive the heating element and an ADC to measure the temperature and close the control loop. The program of the best working clock (\textit{Clock 1}) was extracted and flashed on the \textit{Clock 2 and 3} (listing \ref{lst:flash}).
    
    \begin{lstlisting}[style=bash,label={lst:flash},caption={Read operation to extract microcontroller's binary (Windows CMD).}]
C:\Users\cmrivera\AppData\Local\Arduino15\packages\arduino\tools\avrdude\6.3.0-arduino17/bin/avrdude -CC:\Users\cmrivera\AppData\Local\Arduino15\packages\arduino\tools\avrdude\6.3.0-arduino17/etc/avrdude.conf -v -patmega32u4 -cavr109 -b57600  -PCOM18 -D -Uflash:r:readfile.hex:i
    \end{lstlisting}
    
    \begin{lstlisting}[style=bash,label={lst:flash},caption={Write operation to flash microcontroller's binary (Windows CMD).}]
C:\Users\cmrivera\AppData\Local\Arduino15\packages\arduino\tools\avrdude\6.3.0-arduino17/bin/avrdude -CC:\Users\cmrivera\AppData\Local\Arduino15\packages\arduino\tools\avrdude\6.3.0-arduino17/etc/avrdude.conf -v -patmega32u4 -cavr109 -PCOM18 -b57600 -D -Uflash:w:C:\Users\cmrivera\Desktop\readfile.hex:i 
    \end{lstlisting}
    
    \item \textbf{Connector of external laser temperature controller.}
    \item \textbf{ADC circuit:} In charge of converting the photodiode signal to digital units for the microcontroller. Its resolution can be programmed (see section \ref{section:output_monitoring}).
    \item \textbf{Photodiode signal: } This RF coaxial coupling is connected to the oscilloscope to monitor the photodiode signal.
    \item \textbf{Frequency synthesizer: } Generates the microwave signal necessary to have CPT resonance (see section \ref{section:tp_info}), it consists of a fractional-N frequency synthesizer (ADF4158) connected to a voltage-controlled oscillator (V950ME21-LF) through a loop filter (schematic in figure \ref{fig:sch_synth}). It also provides the modulation to find the error signal for the quartz servo loop, by using FSK (Frequency-shift keying). 
    \item \textbf{Microwave signal attenuator:} In order to control the amount of microwave power mixed with the laser signal, in the practical work, attendees are asked to turn the signal off and then gradually increase it.
    \item \textbf{RF splitter:} To measure the microwave signal.
    \item \textbf{Microwave signal connector: } To monitor the microwave signal on a spectrum analyzer.
    \item \textbf{Component to ensure the microwave signal doesn't reflect into the system.}
    \item \textbf{Physical button:} To interrupt scan or lock processes ran by the microcontroller.
    \item \textbf{USB connector.}
\end{enumerate}

\newpage
\subsection{Improvement of Graphical User Interface and Arduino code}

\subsubsection{Replacement of serial commands by visual control elements}
\label{section:replacement_serial}

To avoid the use of arbitrary and non-intuitive commands on the program's "Console" panel, the complete "Controls" panel was redesigned (as shown in figure \ref{fig:new_gui}), allowing to type in the desired values in labeled boxes and start\slash stop processes with buttons, while the "console commands" were generated and sent to the microcontroller in the background. 

\begingroup
\setlength{\intextsep}{0pt}%
\setlength{\columnsep}{10pt}%
\begin{wrapfigure}{L}{0.4\textwidth}
    % \vspace{-10pt}
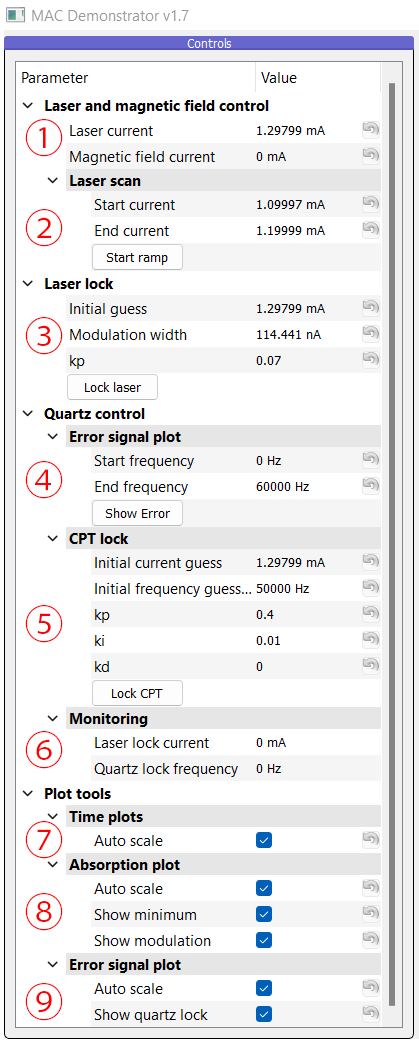
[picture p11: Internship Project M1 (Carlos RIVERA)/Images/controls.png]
    \centering
    \captionsetup{justification=centering}
    \caption{New control panel.}
    \label{fig:new_gui}
\end{wrapfigure}

The description of each control's function will be progressively explained in this report, since they correspond to a specific feature added. Nonetheless, from figure \ref{fig:new_gui} we may identify the following groups:

\begin{enumerate}[wide, labelwidth=!, labelindent=0pt]
	\item \textbf{Laser and magnetic field control:} \newline These two controls were already present in the previous GUI and rely on the console commands \texttt{"9 \{laser current\}"} and  \texttt{"8 \{magnetic field current\}"}, to modify the laser current DAC\footnote{DAC: Digital-to-Analog Converter, is a system that converts a digital signal into an analog signal.} and magnetic field current DAC respectively. %When their value is changed, the commands are replaced with their content and sent to the microcontroller.
	
	\item \textbf{Laser and magnetic field control | Laser scan:} \newline Previously, it was only possible to set the start of the laser ramp with command \mbox{\texttt{"t \{start\}"}}, however this function was modified to also take \mbox{\texttt{"t \{start\} \{end\} \{number of samples\}"}} \break(the \texttt{"number of samples"} was set to 300 by default).
	
	The console command \texttt{"s"}, used to start the ramp process, is now linked with the button "Start ramp".
	\item \textbf{Laser lock:} \newline To lock the laser frequency, it was only possible to select an "initial guess", with the command \mbox{\texttt{"i \{initial guess\}"}}. In order to set the current in the vicinity of the desired absorption. However, the modulation width was fixed at 38.147nA (1 in \textit{machine units}).\newline Now it is also possible to select a modulation width, the graphical controls are linked with the command \mbox{\texttt{"i \{initial guess\} \{modulation width\}"}}. This greatly enhances the locking capability by giving more flexibility to the user, and solved the fact it was difficult to lock with the old program's version. %Explain how the laser lock works so this makes sense.
	\newline The "Lock laser" button is linked with the previous command \texttt{"l"}.
 	\item \textbf{Quartz control | Error signal plot:} \newline In the old version of the program, the command \texttt{"b"} allowed to scan the quartz frequency \textbf{only} from 0 to 41530 (\textit{machine units}) or from 0 to 67.486 kHz. This was improved, and now it is possible to set the "start" and "end" scan frequencies (see section \ref{section:scan_params}).
 	\newline The button "Show Error" is linked with the previous command \texttt{"b"}.
\end{enumerate}
\endgroup

\begin{enumerate}[wide, labelwidth=!, labelindent=0pt]
    \setcounter{enumi}{4} % To set the first number
    \item \textbf{Quartz control | CPT lock:} \newline Formerly, the CPT locking process (locking both servo loops simultaneously) used the commands \mbox{\texttt{"a \{quartz kp\} \{quartz ki\} \{quartz kd\} \{laser kp\}"}} to set the PID parameters and \texttt{"0"} to start. But it was impossible to change the "initial guess" for the frequency offset, this value was hard-coded to be 16.25 kHz.
    \vfill
    After my modifications, it is possible to set an arbitrary "initial guess" frequency and PID parameters from the GUI's entry boxes (see section \ref{section:scan_params}).
    \newline The button "Lock CPT" is linked with the previous command \texttt{"0"}.
    \item \textbf{Quartz control | Monitoring:} \newline This panel of read-only labels was added to have the real-time locking values of the laser and quartz servo loops, and thus, avoid relying on the graphs and graphical estimation.
	\item \textbf{Plot tools | Time plots:} \newline An option to enable or disable auto-scale from the plots was added. 
	\item \textbf{Plot tools | Absorption plot:} \newline  Two visual aid tools were implemented for the absorption profile graph: A minimum value marker (see section \ref{section:max_absorb}) and a pair of lock modulation markers (see section \ref{section:lock/unlock}).

	\item \textbf{Plot tools | Error signal plot:} \newline A lock offset frequency marker was added for both the "Error signal" and "CPT signal" plots. Which allow monitoring in real time the locking status of the demonstrator (see section \ref{section:lock/unlock}).
	
% 	\begin{figure}[!h]
%     \centering
%     \includegraphics[width=0.6\textwidth]{Images/plot_tools_2.png}
%     \captionsetup{justification=centering}
%     \caption{Plot tools for the CPT and Error signal} 
%     \label{fig:plot_tools_2}
%     \end{figure}
\end{enumerate}

\subsubsection{Conversion from machine units to physical units}
\label{section:physical_units}

One of the main shortcomings the project presented at the beginning of my internship, was the fact that both the commands to control the demonstrator, and the graphs of the GUI were in \textit{machine units}. Since these were the values that the microcontroller handled with the ADC and DAC and no conversion mechanism was implemented yet.

This lead to a non-intuitive experience for the seminar attendees, that were not able to work with real physical units and thus, not fully conceptualize the theoretical information received. 

The solution was to determine a linear relation between the machine and physical units. First, by carrying-out measurements that later were used to fit a curve with the correct coefficients needed to create conversion functions for both the microcontroller and the Python GUI.
\subsubsubsection{Machine units to photodiode voltage and vice-versa}
\label{section:word_to_volt}
In order to create a conversion function, it was necessary to determine the correct coefficients for a linear fit. To do this, five arbitrary laser current values were set, and the photodiode output was measured both with the demonstrator's ADC and with a connected oscilloscope. The results are shown in figure \ref{fig:word_to_volt}, as expected a linear relation can be extracted.

\begin{figure}[!h]
    \centering
    
    \captionsetup{justification=centering}
    \caption{Comparison between ADC and photodiode voltage measurements.} 
    \label{fig:word_to_volt}
\end{figure}

The linear fit was computed with MATLAB (file: Conversion\_Functions\_Coefficients.m) and the coefficients in equation \ref{eq:word_to_volt_1} were found, and the expressions at equation \ref{eq:word_to_volt_2} deduced.
\begin{align}
y=p1*x+p2\quad
\begin{cases}
p1=\SI{3.0295e-05}{}\\ p2=2.4539
\end{cases}
\label{eq:word_to_volt_1}
\\voltage=p1*ADC+p2 \quad\text{and}\quad ADC=\frac{(voltage-p2)}{p1}
\label{eq:word_to_volt_2}
\end{align}

To verify the conversion factor, an arbitrary point in the absorption profile was selected and the measurements between the GUI and oscilloscope were compared. As shown in figure \ref{fig:word_to_volt_ver}, the values are close enough. 
As per equation \ref{eq:word_to_volt_2}, the implemented conversion functions are presented in listing \ref{lst:word_to_volt}.

\begin{figure}[!h]
\centering
\begin{subfigure}[b]{0.85\textwidth}
	\centering
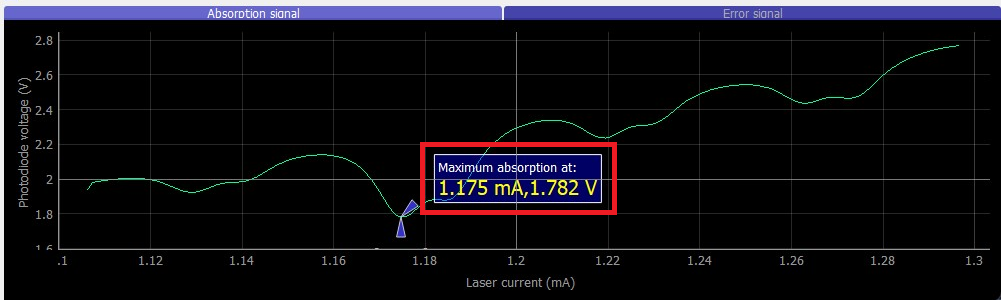
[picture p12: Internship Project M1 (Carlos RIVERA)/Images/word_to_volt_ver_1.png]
	
	\captionsetup{justification=centering}
\end{subfigure}
\newline
\begin{subfigure}[b]{0.85\textwidth}
	\centering
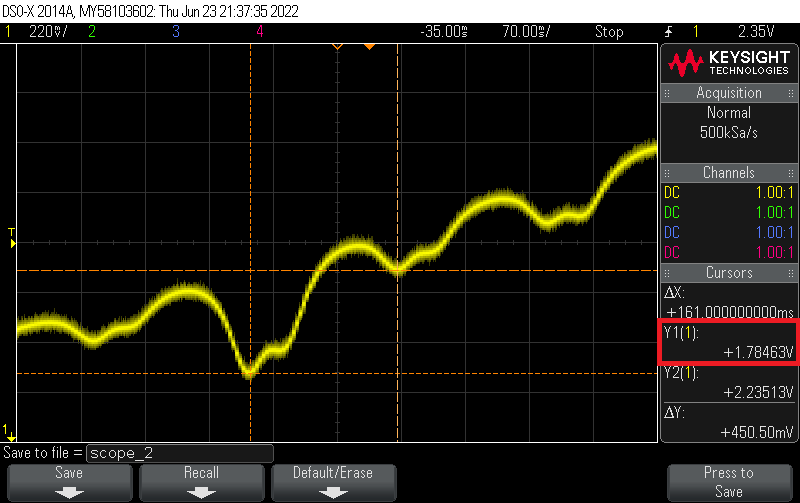
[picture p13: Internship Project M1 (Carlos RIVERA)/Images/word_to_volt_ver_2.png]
	
	\captionsetup{justification=centering}
\end{subfigure}
 \caption{Conversion factor verification for the word to voltage function.}
\label{fig:word_to_volt_ver}
\end{figure}

\begin{lstlisting}[style=python,label={lst:word_to_volt},caption={Python functions to convert machine units to voltage (file: misc.py).},firstnumber=151,escapeinside={\%}{\%}]
def word_to_voltage(value): %\addtocounter{lstnumber}{1}%
    p1=0.000030294604198194861416565740186435
    p2=2.4538899853718616483888581569772 %\addtocounter{lstnumber}{4}%
    return p1*value+p2

def voltage_to_word(value): %\addtocounter{lstnumber}{1}%
    p1=0.000030294604198194861416565740186435
    p2=2.4538899853718616483888581569772 %\addtocounter{lstnumber}{4}%
    return int((value-p2)/p1)
\end{lstlisting}
\subsubsubsection{Machine units to frequency offset and vice-versa}

Similar to the previous section (see \ref{section:word_to_volt}), we wish to determine the correct coefficients and linear relation between the set values for the quartz's DAC and the frequency shift (measured with a spectrum analyzer). To do this, 14 measurements were performed, and plotted in figure \ref{fig:word_to_freq}.

\begin{figure}[!h]
    \centering
    
    \captionsetup{justification=centering}
    \caption{Comparison between quartz's DAC and frequency offset measurements.} 
    \label{fig:word_to_freq}
\end{figure}

Since only the frequency offset is required, the coefficient "$p2$" is disregarded. The resulting equations (equation \ref{eq:word_to_freq_1} and \ref{eq:word_to_freq_2}) were implemented in python, as shown in listing \ref{lst:word_to_frequency}.
\begin{align}
y=p1*x+p2\quad
\begin{cases}
p1=1.6250\\ p2=\SI{7.4299e-12}{} \approx 0
\end{cases}
\label{eq:word_to_freq_1}
\\frequency=p1*DAC \quad\text{and}\quad DAC=\frac{frequency}{p1}
\label{eq:word_to_freq_2}
\end{align}
\begin{lstlisting}[style=python,label={lst:word_to_frequency},caption={Python functions to convert machine units to frequency offset (file: misc.py).},firstnumber=171]
def word_to_frequency(value):
    p1=1.625
    p2=0
    return p1*value+p2

def frequency_to_word(value):
    p1=1.625
    p2=0
    return int((value-p2)/p1)
\end{lstlisting}

\subsubsubsection{Machine units to laser current and vice-versa}
\label{section:word_to_current}
The function to convert laser current to machine units was already present in the code. In listing \ref{lst:word_to_current}, the python class "LaserCurrentSource" contains a "setter decorator" method (line 49) that converts the input value (in mA) to machine units (line 52) and sends the appropriate command (line 53).

\begin{lstlisting}[style=python,label={lst:word_to_current},caption={Python function to convert laser current to machine units (file: mac\_device.py).},firstnumber=49]
@current.setter
def current(self, value):
    assert 0 <= value < 1.7
    self._current_word = int((value/2.5)*2.**16)
    self.parent.send("9 " + str(self._current_word))
\end{lstlisting}

\subsubsubsection{Machine units to magnetic field current and vice-versa}
Just as in the previous section (\ref{section:word_to_current}), the function to convert magnetic field current to machine units was present in the code as part of a "setter decorator" method, as shown in listing \ref{lst:word_to_mag}.

\begin{lstlisting}[style=python,label={lst:word_to_mag},caption={Python function to convert magnetic field current to machine units (file: mac\_device.py).},firstnumber=65]
@current.setter
def current(self, value):
    assert 0 <= value < 50
    self._current_word = int(value / 50. * (2.**16))
    logging.debug(self._current_word)
    self.parent.send("8 " + str(self._current_word))
\end{lstlisting}

% \subsubsection{Modification of Control panel elements}
% \label{section:control_elements}

\subsubsection{Flexibility to choose quartz oscillator scan and lock parameters}
\label{section:scan_params}

Due to the limitations of the previous quartz functions, two new commands have been added to the microcontroller code. First, the "start" and "end" frequencies for the quartz scan are no longer hard-coded, and it's possible to change them with the command \mbox{\texttt{"v \{start\} \{end\}"}} (listing \ref{lst:v_command}).

\begin{lstlisting}[style=c++,label={lst:v_command},caption={Command to change the quartz's scan parameters (file: mac.ino).},firstnumber=483]
//case 'v':
void QuartzScanSetStart(){
  scanQuartzStart=Serial.parseInt();
  scanQuartzEnd=Serial.parseInt();  
}
\end{lstlisting}

And lastly, the "initial guess" and "offset" for the quartz lock frequency can be changed with the command \mbox{\texttt{"j \{initial guess\} \{offset\}"}} (listing \ref{lst:j_command}).

\begin{lstlisting}[style=c++,label={lst:j_command},caption={Command to change the quartz's lock "initial guess" frequency (file: mac.ino).},firstnumber=472]
//case 'j':
void setQuartzLockParameters(){
  quartz_init = Serial.parseFloat();
  quartz_offset = Serial.parseFloat();
}
\end{lstlisting}

Both commands are linked with their respective graphical control elements.

\subsubsection{Interruption of processes through GUI}
\label{section:stop_process}

In the old version of the demonstrator program (version 1.6), it was necessary to press a physical button (mounted on the external housing) in order to interrupt a scan or lock process. This was not practical and introduced vibrations to the system. This is why a GUI solution was convenient.

Every button in the GUI has a double function, for example as shown in listing \ref{lst:button_function}, when the "Lock CPT" button is pressed, the lock process starts (line 662) and its name changes to "Unlock CPT" (line 661). Thus, next time the button is pressed, since its name is no longer "Lock CPT" (condition of line 660), the "else" statement of line 664 to 665 is executed.

\begin{lstlisting}[style=python,label={lst:button_function},caption={Double function for GUI buttons (file: qt\_mac.py).},firstnumber=659]
def action_start_CPT_lock(self):
    if("Lock CPT" == self.btn_start_CPT_lock.name()):
        self.btn_start_CPT_lock.setName("Unlock CPT")
        self.mac.lock_cpt()
    else:
        self.btn_start_CPT_lock.setName("Lock CPT")
        self.mac.stop_signal()
\end{lstlisting}

The "stop\_signal()" method sends the character "x" to the demonstrator microcontroller (listing \ref{lst:stop_signal}).

\begin{lstlisting}[style=python,label={lst:stop_signal},caption={Stop signal method (file: mac\_device.py).},firstnumber=245]
def stop_signal(self):
    self.send("x")
\end{lstlisting}

Previously, the only way to stop a process was by pressing the external physical button (e.g. in the laser lock function, listing \ref{lst:stop_methods}, line 515). Now there is also a condition, checked at every iteration, that if the character "x" is received from the GUI, the loop must be exited (line 516 to 520).

\begin{lstlisting}[style=c++,label={lst:stop_methods},caption={Stop signal methods in laser lock function (file: mac.ino).},firstnumber=515]
while(ButtonState == LOW){
    if(Serial.available()){
        if((char)Serial.read()=='x'){
            break;
        }
    }
\end{lstlisting}

\subsubsection{Photodiode output monitoring independent of oscilloscope}
\label{section:output_monitoring}

Originally, the demonstrator could only be used by relying on an oscilloscope connected to the photodiode output, this defeated the purpose of having a compact, all contained device. This is why it was decided to add a graph with the photodiode signal (through an ADC), as presented in figure \ref{fig:absorption_graph}.

\begin{figure}[!h]
    \centering
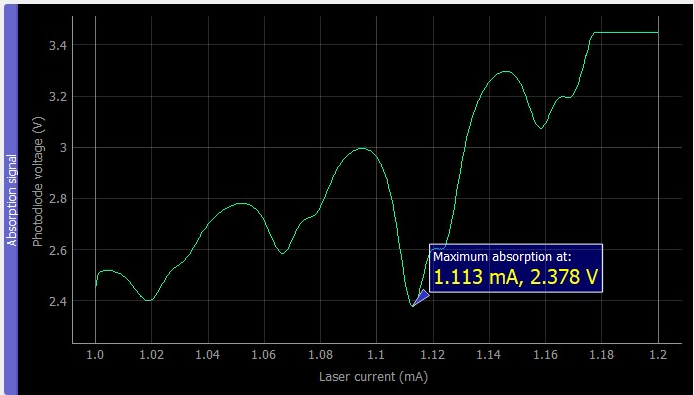
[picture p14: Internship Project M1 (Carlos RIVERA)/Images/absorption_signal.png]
    
    \captionsetup{justification=centering}
    \caption{"Absorption signal" plot feature.} 
    \label{fig:absorption_graph}
\end{figure}

In the practical work, students are asked to estimate the threshold current of the VCSEL\footnote{VCSEL: Vertical-cavity surface-emitting laser, is a type of semiconductor laser diode with laser beam emission perpendicular from the top surface.} laser of the demonstrator. The threshold current of a laser is the current value at which the laser output power stops being 0 V and becomes linear, in other words, the value at which the laser emission can begin.

To find the threshold current of the laser, a scan from 0 to 1.7 mA (the maximum current used in the demonstrator) must be performed. However, a limitation was found. The ADC was able to measure only a fraction of the signal, as shown between the oscilloscope cursors in figure \ref{fig:adc_limitation}, the applied ramp went from 0 to 5 V, but the ADC measured only the values between 1.46 and 3.4 V approximately.
%picture
\begin{figure}[!h]
\centering
\begin{subfigure}[b]{0.49\textwidth}
	\centering
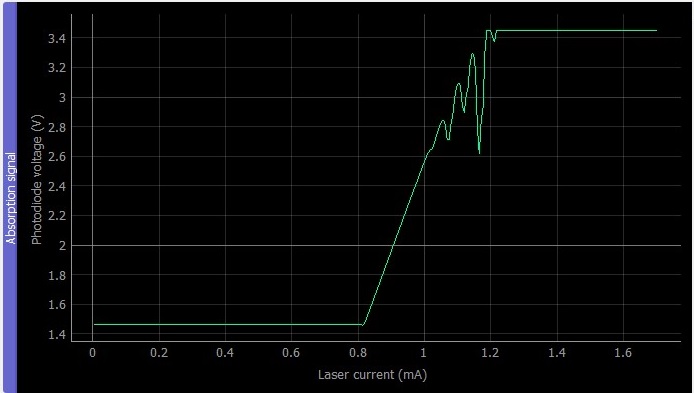
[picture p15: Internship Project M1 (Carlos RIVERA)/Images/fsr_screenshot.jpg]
	
	\captionsetup{justification=centering}
\end{subfigure}
\hfill
\begin{subfigure}[b]{0.49\textwidth}
	\centering
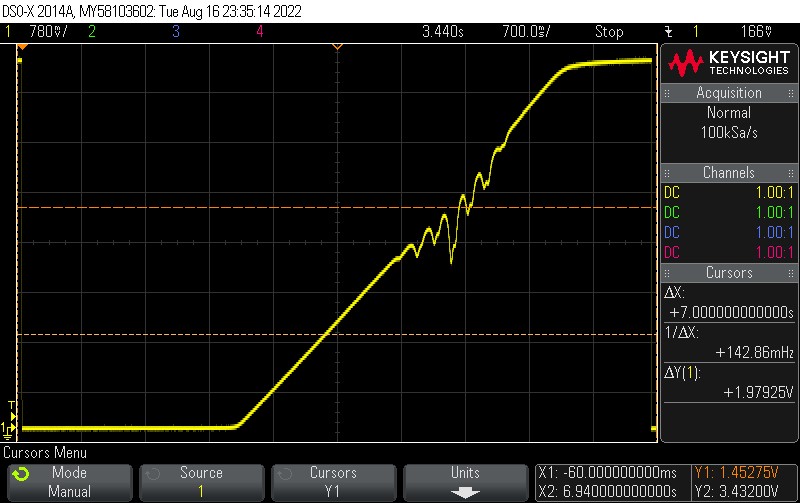
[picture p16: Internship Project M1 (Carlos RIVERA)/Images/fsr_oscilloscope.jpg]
	
	\captionsetup{justification=centering}
\end{subfigure}
 \caption{Demonstrator's ADC limitation found.}
\label{fig:adc_limitation}
\end{figure}

Due to this limitation, it is imperative to use the oscilloscope, at least for the first part of the practical work. After analyzing the microcontroller code, it was found the ADC initialization function (listing \ref{lst:ADC_init}). The bits sent over SPI communication indicated that the FSR\footnote{FSR: Full-Scale Range of the ADC scaling that relies on the internal programmable gain amplifier (PGA).} was set to \mbox{1.024 V} (according to the ADC ADS1118 datasheet).
%listing
\begin{lstlisting}[style=c++,label={lst:ADC_init},caption={ADC\_startup() function (file: mac.ino).},firstnumber=421,literate={mu}{$\mu$}1]
void ADC_startup() { // Starts ADS1118, FSR = 1.024 V
  SPI.setDataMode(SPI_MODE1);
  digitalWrite(CS_ADC, LOW);
  SPI.transfer(B00000110); // CR: ADC FSR = 1.024V, since Ref is 2.5 V, 
  SPI.transfer(B11100011); // CR: the measurement range is from 1.4760 V to 3.5240 V
  digitalWrite(CS_ADC, HIGH); // CR: with a LSB size of 31.25 muV (LSB = FSR / 2^16).
  SPI.setDataMode(SPI_MODE0);
}
\end{lstlisting}

Upon analysis of the ADC schematic (figure \ref{fig:adc_sch}) it was found that the reference value of the ADC is 2.5 V (ADM7150 voltage regulator). Thus, the full measure range of the ADC was determined in equation \ref{eq:full_range_1}.
%schematic
\begin{figure}[!h]
    \centering
    
    \captionsetup{justification=centering}
    \caption{ADC schematic.} 
    \label{fig:adc_sch}
\end{figure}

%equation
\begin{align}
\text{FSR} &= \pm 1.024\; V\nonumber\\
\text{Measure range}&=2.5 \pm \text{FSR} V\nonumber\\
\text{Measure range}&= 1.4760 \text{ V to } 3.5240 \text{ V}
\label{eq:full_range_1}
\end{align}

The LSb resolution\footnote{The LSb resolution represents the smallest interval that can be detected by the ADC.} was calculated to be $31.25 \;\mu \mathrm{V}$ (equation \ref{eq:lsb}).

\begin{align}
\text{LSb} &= \text{FSR}/2^{16} \nonumber\\
\text{LSb} &= \text{1.024}/2^{16} = 31.25 \;\mu \mathrm{V}
\label{eq:lsb}
\end{align}

In order to have a bigger measuring range, a compromise between FSR and LSb resolution must be made, as shown in table \ref{table:FSR}. To measure values from 0 to 5 V, the FSR of $\pm 4.096 \;\mathrm{V}$ must be selected. 

%table
\begin{table}[h!]
\centering
\begin{tabular}{|c|r|}
\hline
\textbf{FSR} & \textbf{LSb size} \\ \hline
$\pm$6.144 V     & 187.5 $\mu$V          \\ \hline
$\pm$4.096 V     & 125 $\mu$V            \\ \hline
$\pm$2.048 V     & 62.5 $\mu$V           \\ \hline
$\pm$1.024 V     & 31.25 $\mu$V          \\ \hline
$\pm$0.512 V     & 15.625 $\mu$V         \\ \hline
$\pm$0.256 V     & 7.8125 $\mu$V         \\ \hline
\end{tabular}
\caption{Full-scale range and corresponding LSb table.}
\label{table:FSR}
\end{table}
%Results of test (pending)
The new FSR function (listing \ref{lst:ADC_init_2}) was tested on \textit{Clock 1} and the results are presented in figure \ref{fig:adc_limitation_fixed}.

\begin{lstlisting}[style=c++,label={lst:ADC_init_2},caption={ADC\_startup() recommended function (file: mac.ino).},firstnumber=431,literate={mu}{$\mu$}1]
void ADC_startup() { // Starts ADS1118, FSR = 4.096 V
  SPI.setDataMode(SPI_MODE1);
  digitalWrite(CS_ADC, LOW);
  SPI.transfer(B00000010); // CR: ADC FSR = 4.096V, since Ref is 2.5 V, 
  SPI.transfer(B11100011); // CR: the measurement range is from -1.596 V to 6.596 V*
  digitalWrite(CS_ADC, HIGH); // CR: with a LSB size of 125 muV (LSB = FSR / 2^16).
  SPI.setDataMode(SPI_MODE0); // *Note: photodiode outputs never exceeds 6 V.
}
\end{lstlisting}

\begin{figure}[!h]
\centering
\begin{subfigure}[b]{0.49\textwidth}
	\centering
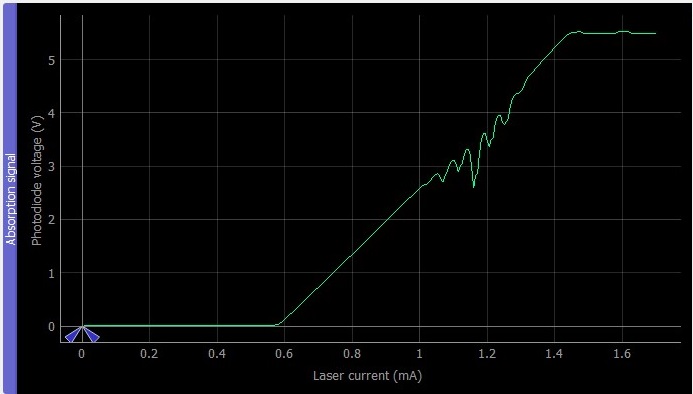
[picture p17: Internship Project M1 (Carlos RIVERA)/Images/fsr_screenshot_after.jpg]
	
	\captionsetup{justification=centering}
\end{subfigure}
\hfill
\begin{subfigure}[b]{0.49\textwidth}
	\centering
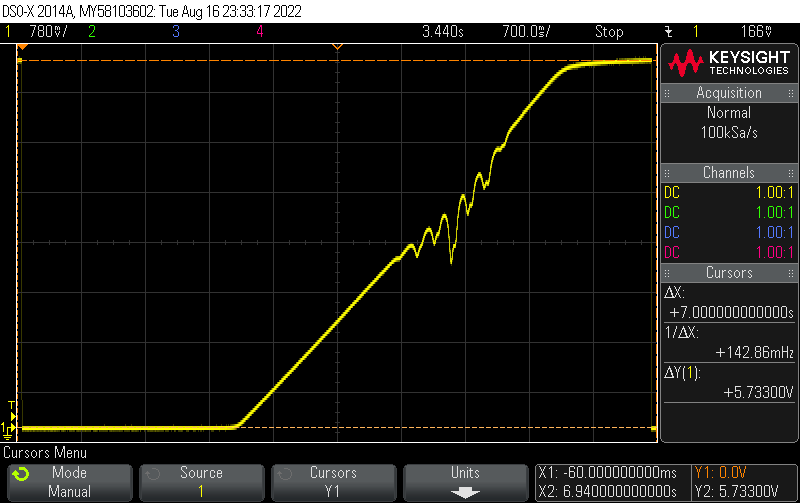
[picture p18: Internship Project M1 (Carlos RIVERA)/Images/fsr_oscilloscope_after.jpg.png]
	
	\captionsetup{justification=centering}
\end{subfigure}
 \caption{Demonstrator's ADC limitation fixed.}
\label{fig:adc_limitation_fixed}
\end{figure}

After this modification it was necessary to recalculate the coefficients that allow the conversion from machine units to volts, the linear fit was computed with MATLAB from a new data set obtained from measuring the ADC value in machine units and its corresponding voltage value measured with the oscilloscope. The new coefficients and mathematical expression are found in equation \ref{eq:word_to_volt_1_2} and \ref{eq:word_to_volt_2_2}. The resulting fit presented in figure \ref{fig:word_to_volt_new} confirms the linear relation.

%Add equation and fit
\begin{align}
y=p1*x+p2\quad
\begin{cases}
p1=\SI{1.2448e-04}{}\\ p2=2.4863
\end{cases}
\label{eq:word_to_volt_1_2}
\\voltage=p1*ADC+p2 \quad\text{and}\quad ADC=\frac{(voltage-p2)}{p1}
\label{eq:word_to_volt_2_2}
\end{align}

\begin{figure}[!h]
    \centering
    
    \captionsetup{justification=centering}
    \caption{Improved linear fit between ADC and photodiode voltage measurements.} 
    \label{fig:word_to_volt_new}
\end{figure}

Finally, the new conversion functions are shown in listing \ref{lst:word_to_voltage_new}.
%Add listing

\begin{lstlisting}[style=python,label={lst:word_to_voltage_new},caption={Improved Python functions to convert machine units to voltage (file: misc.py).},firstnumber=151]
def word_to_voltage(value):
    #For FSR = 1.024 V
    # p1=0.000030294604198194861416565740186435
    # p2=2.4538899853718616483888581569772

    #For FSR = 4.096 V
    p1=0.00012448304623130003205427884793721
    p2=2.4863253857628526688472447858658
    return p1*value+p2
    
def voltage_to_word(value):
    #For FSR = 1.024 V
    # p1=0.000030294604198194861416565740186435
    # p2=2.4538899853718616483888581569772

    #For FSR = 4.096 V
    p1=0.00012448304623130003205427884793721
    p2=2.4863253857628526688472447858658
    return int((value-p2)/p1)
\end{lstlisting}

To confirm that the new reduced resolution did not affect the normal operation of the clocks, the \textit{Clock 1} was successfully locked on its CPT signal, as shown in figure \ref{fig:ADC_fix_check_CPT_lock}.

\begin{figure}[!h]
    \centering
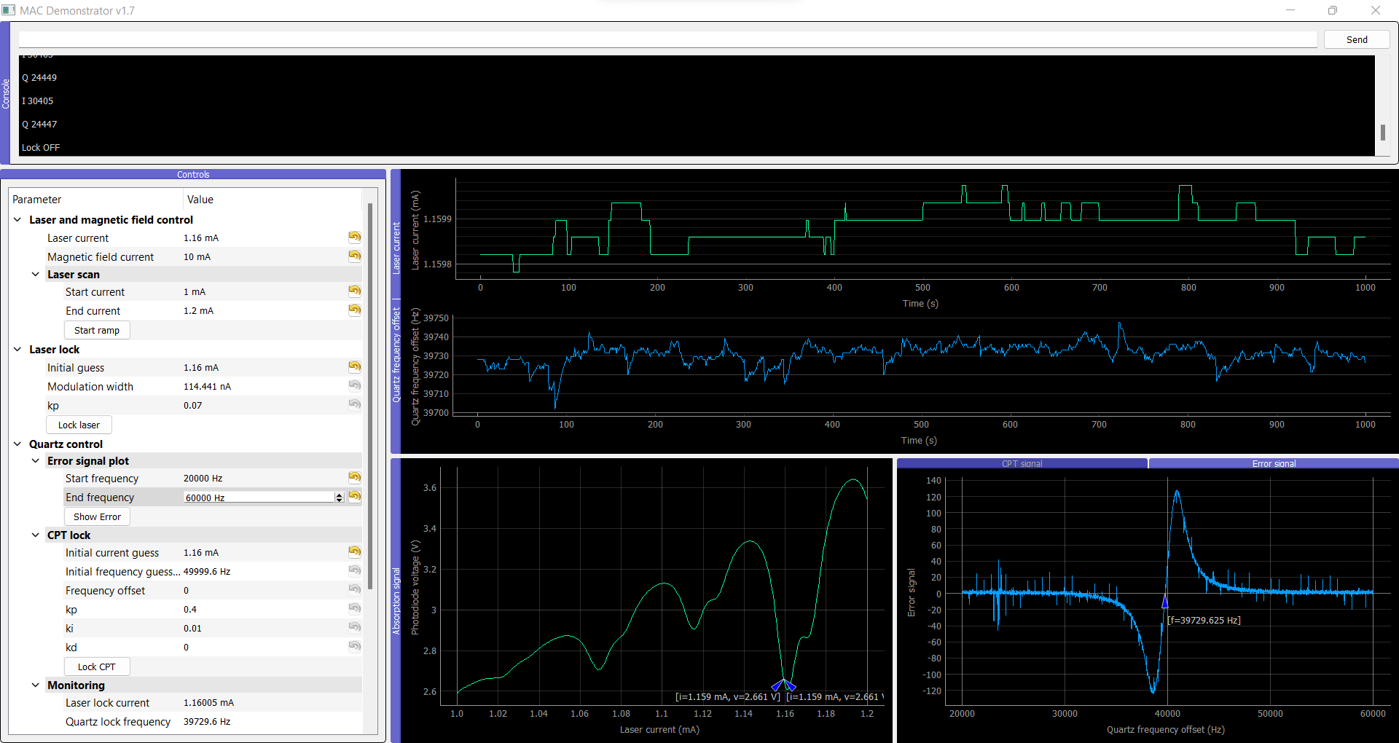
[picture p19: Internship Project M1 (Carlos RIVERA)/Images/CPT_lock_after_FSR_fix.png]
    
    \captionsetup{justification=centering}
    \caption{\textit{Clock 1} locked to its CPT signal after ADC limitation fixed.} 
    \label{fig:ADC_fix_check_CPT_lock}
\end{figure}

%
\newpage
\subsubsection{Addition of graph titles and axis labels}
\label{section:graphs}

All graphs were missing titles and axis labels, which resulted in a difficult to understand interface. In the new version, all the graphs are correctly labeled.

\subsubsection{Precise identification of maximum absorption}
\label{section:max_absorb}
 As shown in figure \ref{fig:plot_tools_1} a marker that indicates the minimum value found within the current measurement scope was implemented. This allows a precise identification of the laser current value at which the maximum absorption is found. 

\begin{figure}[!h]
\centering
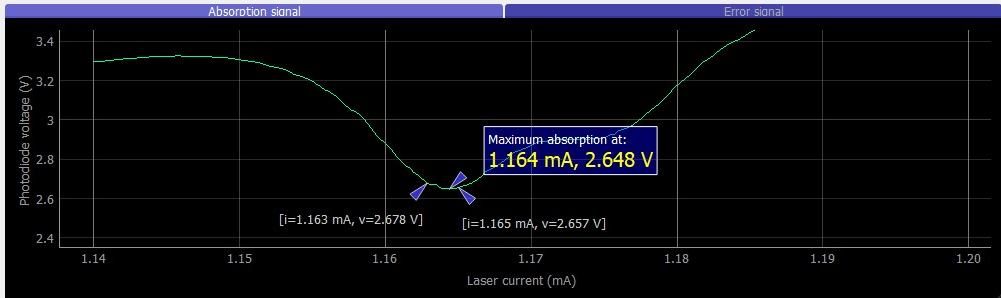
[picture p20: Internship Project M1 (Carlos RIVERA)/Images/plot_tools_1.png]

\captionsetup{justification=centering}
\caption{Plot tools for the absorption graph} 
\label{fig:plot_tools_1}
\end{figure}

\newpage    
\subsubsection{Graphical identification of locked/unlocked servo loops}
\label{section:lock/unlock}
%Explain lock and modulation

For didactic purposes, two separate arrow markers that highlight the current modulation measurement points were implemented in the "Absorption signal" graph (these markers become red if the lock state is lost and out of scope). The laser current value corresponding to the lock location is found at the middle of the modulation (figure \ref{fig:plot_tools_1}).

Similar to the previously described feature, it was desired to have a visual indicator of the quartz servo loop lock state (these markers become red if the lock state is lost and out of scope). As presented in figure \ref{fig:plot_tools_2}, now it's possible to visualize the locking offset frequency in both the CPT and Error signal graphs.
\begin{figure}[!h]
\centering
\begin{subfigure}[b]{0.49\textwidth}
\centering
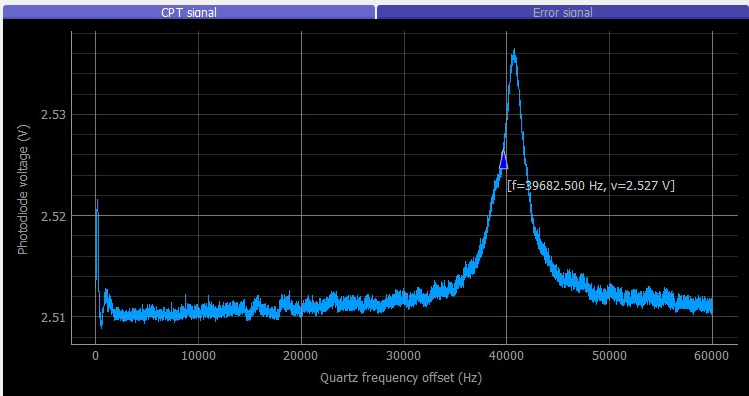
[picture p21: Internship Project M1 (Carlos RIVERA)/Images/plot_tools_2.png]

\captionsetup{justification=centering}
\caption{CPT signal plot}
\label{fig:cpt_signal}
\end{subfigure}
\hfill
\begin{subfigure}[b]{0.49\textwidth}
\centering
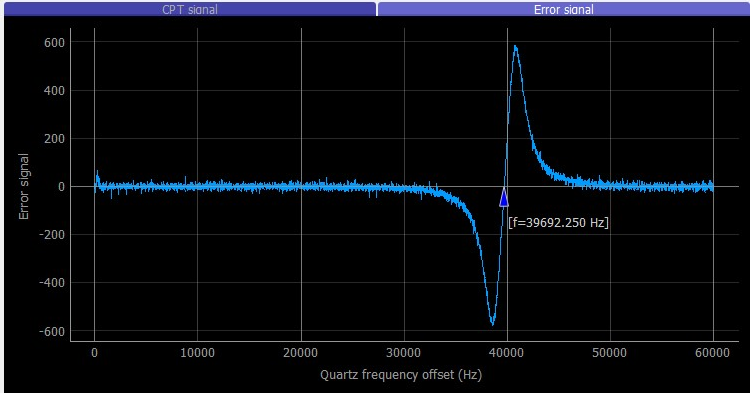
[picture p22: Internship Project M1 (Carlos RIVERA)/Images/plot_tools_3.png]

\captionsetup{justification=centering}
\caption{Error signal plot}
\label{fig:error_signal}
\end{subfigure}
\caption{Plot tools for the CPT and Error signal} 
\label{fig:plot_tools_2}
\end{figure}
    
\subsubsection{Visualization of CPT signal}
\label{section:CPT}

In the original software, it was only possible to plot the error signal after a quartz scan (figure \ref{fig:error_signal}). We decided to also add the CPT transmission signal to the GUI for pedagogical purposes \mbox{(figure \ref{fig:cpt_signal})}.

\subsection{Measuring atomic clock stability}

To determine the stability of the atomic clock, we compute its Allan variance, which is a common way of characterizing the various sources of noise that can affect a clock stability. 

The instantaneous clock frequency $f_n$ is measured with an interval $\tau$, and we compute its mean value $<f>$. We then calculate the relative (or fractional) frequency $y_n = f_n / <f>$.
The Allan deviation is a measurement of the fractional frequency fluctuations for various integration times $\tau$.

The Allan variance for an integration time $\tau$ is given by:

\begin{equation}
\sigma^2 (\tau) = \frac{1}{2}* \langle (y_{n+1}-y_n)^2 \rangle
\end{equation}

%Consider the error measurements of a clock $x_n$, $x_{n+1}$, $x_{n+2}$ within interval $\tau$ \cite{allan1997science}. The normalized frequency departure average is 
% \begin{equation}
%     y_n = \frac{\Delta x_n}{\tau}
% \label{eq:average}
% \end{equation}
% The Allan variance is
% \begin{equation}
%     \sigma^{2} = \frac{1}{2\tau^{2}}(\Delta y^{2})
% \end{equation}
% Where $y$ is the normalized average frequency departure for the interval of $\tau$.
The Allan deviation is $\sigma$, the square root of the variance. The advantage of the Allan variance over standard variance is that the former can diverge for different types of noise independently of the number of samples. Another way to quantify the frequency instability is through the modified Allan deviation, which can differentiate between white noise and flicker PM noise. The purpose behind computing the Allan variance is that, ideally, the frequency spectrum is a straight line. However, due to noise, the frequency fluctuates between several values. The Allan variance quantifies how stable the frequency is through averaging the frequency over a certain average time. Practically, we select $\tau$ as an integration time and try to reconstruct the frequency signal by calculating the average. In this application, the instrument that we connected to measure the average and the Allan deviation is the Microsemi\slash Symmetricom 5120A, shown in figure \ref{fig:5125A}.

\begin{figure}[!h]
    \centering
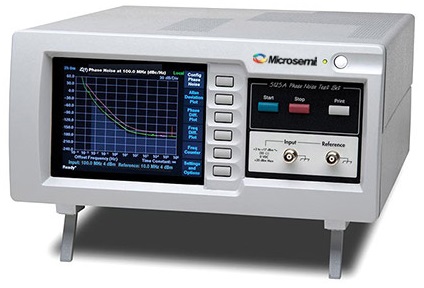
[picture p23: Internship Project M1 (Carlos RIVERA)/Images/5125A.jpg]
    
    \captionsetup{justification=centering}
    \caption{Microsemi\slash Symmetricom instrument to measure Allan deviation} 
    \label{fig:5125A}
\end{figure}

We use figures \ref{fig:allan01}-\ref{fig:allan14} to illustrate Allan deviation measurements (the fractional frequency vs time data on the left were not taken for the CPT clocks, but this does not change the interpretation). \mbox{Figure \ref{fig:allan01}} corresponds to the smallest integration time, $\tau = 0.68\; s$. The fractional frequency fluctuations are $3x10^{-10}$. Figure \ref{fig:allan08} corresponds to an integration time of $86.8 s$ between each point. The relative frequency fluctuations are then much smaller, of about $2x10^{-11}$. Then finally, as shown in figure \ref{fig:allan14}, as $\tau$ increases, the Allan deviation is improved until a certain threshold where is reaches its minimum. After this threshold, increasing $\tau$ results in a frequency instability.

\begin{figure}[!h]
    \centering
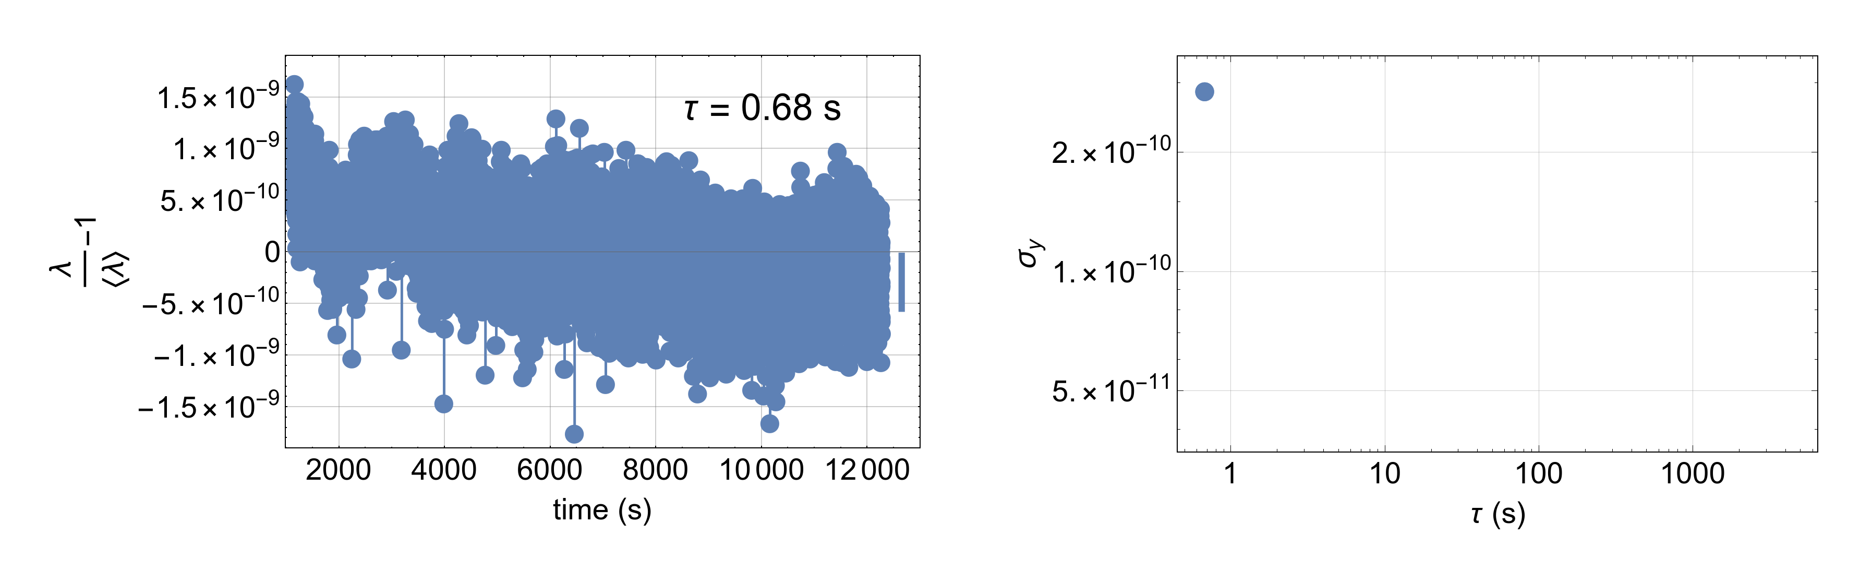
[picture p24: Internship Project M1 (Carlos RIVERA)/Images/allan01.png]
    
    \captionsetup{justification=centering}
    \caption{Short term stability} 
    \label{fig:allan01}
\end{figure}
\begin{figure}[!h]
    \centering
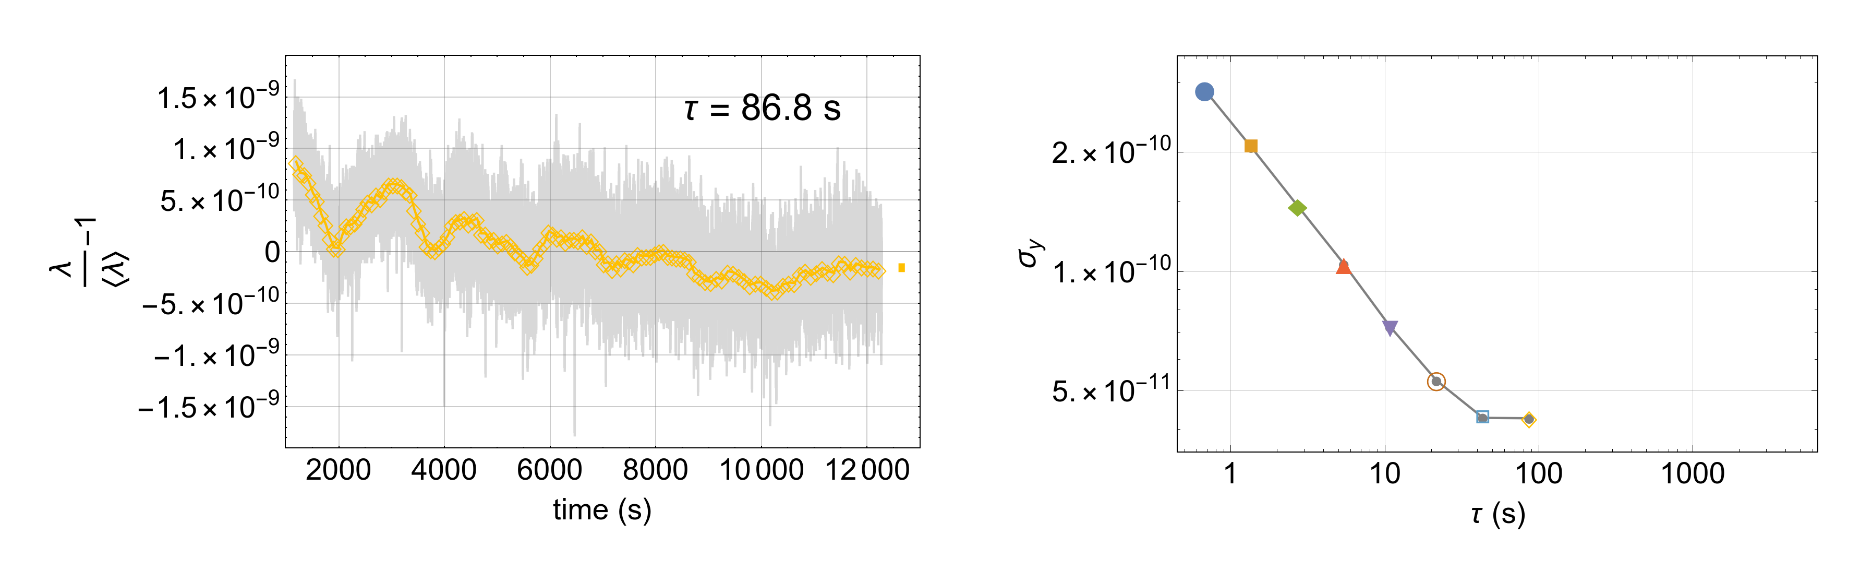
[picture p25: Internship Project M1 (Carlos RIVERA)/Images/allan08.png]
    
    \captionsetup{justification=centering}
    \caption{Minimum Allan deviation threshold} 
    \label{fig:allan08}
\end{figure}
\begin{figure}[!h]
    \centering
    
    \captionsetup{justification=centering}
    \caption{Frequency instability} 
    \label{fig:allan14}
\end{figure}
\break
The Allan deviation of the free running quartz and quartz with locked servo loops was measured through the instrument. The values were extracted and plotted on MATLAB as shown in figure \ref{fig:stability_comp}. An important parameter when computing the Allan deviation is the average at 1 second, since it determines the short term stability. The free running quartz has a better short term stability than the one with locked servo loops. However, the latter is more stable with time, whereas the former loses the short term stability and becomes unstable after a certain period of time. The phase noise floor of the machine determines the threshold of the instrument sensitivity. In other words, measurements taken below the phase noise floor might not be as accurate.

\begin{figure}[!h]
    \centering
    
    \captionsetup{justification=centering}
    \caption{Frequency stability comparison.} 
    \label{fig:stability_comp}
\end{figure}

% \subsection{Creation of documentation based on Arduino and Python code}
% \subsection{Implementation of unit tests for debugging purposes}

%Repair section:
\subsection{Repair of the two not working Atomic clocks}
\label{section:repair_atomic_clocks}

Two of the three atomic clock demonstrators were not operational, like \textit{Clock 2}, as shown in \mbox{figure \ref{fig:not_working_1}}. It could be identified a weak middle absorption, a very low signal-to-noise ratio, and both the "Error" and "CPT" signals were almost non-existent.

\begin{figure}[!h]
    \centering
    
    \captionsetup{justification=centering}
    \caption{\textit{Clock 2} not working properly.} 
    \label{fig:not_working_1}
\end{figure}

First, it was decided to test the Physical Packages of each clock (which is the combination of the Cs vapor cell, optics, laser, photodiode, heating element and magnetic field coil). The reason behind testing them is to determine if this was the root cause of the issue, considering that the three demonstrators were supposed to be identical.

As shown in figure \ref{fig:pp_test}, all the Physical Packages were working correctly when installed in the best working clock taken as reference (\textit{Clock 1}).

%PP1
\begin{figure}[!h]
\centering
\begin{subfigure}[b]{0.49\textwidth}
\centering

\captionsetup{justification=centering}
\caption{Error signal: Physical Package 1 in \textit{Clock 1}.}
\end{subfigure}
\hfill
\begin{subfigure}[b]{0.49\textwidth}
\centering

\captionsetup{justification=centering}
\caption{CPT signal: Physical Package 1 in \textit{Clock 1}.}
\end{subfigure}

%PP2
\centering
\begin{subfigure}[b]{0.49\textwidth}
\centering

\captionsetup{justification=centering}
\caption{Error signal: Physical Package 2 in \textit{Clock 1}.}
\end{subfigure}
\hfill
\begin{subfigure}[b]{0.49\textwidth}
\centering

\captionsetup{justification=centering}
\caption{CPT signal: Physical Package 2 in \textit{Clock 1}.}
\end{subfigure}

%PP3
\centering
\begin{subfigure}[b]{0.49\textwidth}
\centering

\captionsetup{justification=centering}
\caption{Error signal: Physical Package 3 in \textit{Clock 1.}}
\end{subfigure}
\hfill
\begin{subfigure}[b]{0.49\textwidth}
\centering

\captionsetup{justification=centering}
\caption{CPT signal: Physical Package 3 in \textit{Clock 1}.}
\end{subfigure}

\caption{Test of Physical packages in reference \textit{Clock 1}} 
\label{fig:pp_test}
\end{figure}

The next troubleshooting step was to test the microwave synthesizers in the best working clock (\textit{Clock 1}) to compare the results. As shown in figure \ref{fig:synth_test}, the synthesizer 1 and 2 have an incorrect "Error signal" and a very weak "CPT signal" which indicated an erratic modulation.

\begin{figure}[!h]
%PP2
\centering
\begin{subfigure}[b]{0.49\textwidth}
\centering

\captionsetup{justification=centering}
\caption{Error signal: Synthesizer 2 in \textit{Clock 1}.}
\end{subfigure}
\hfill
\begin{subfigure}[b]{0.49\textwidth}
\centering

\captionsetup{justification=centering}
\caption{CPT signal: Synthesizer 2 in \textit{Clock 1}.}
\end{subfigure}

%PP3
\centering
\begin{subfigure}[b]{0.49\textwidth}
\centering

\captionsetup{justification=centering}
\caption{Error signal: Synthesizer 3 in \textit{Clock 1.}}
\end{subfigure}
\hfill
\begin{subfigure}[b]{0.49\textwidth}
\centering

\captionsetup{justification=centering}
\caption{CPT signal: Synthesizer 3 in \textit{Clock 1}.}
\end{subfigure}

\caption{Test of Synthesizers in reference \textit{Clock 1}} 
\label{fig:synth_test}
\end{figure}

The synthesizer circuit consists of a ADF4158 fractional-N frequency synthesizer (maximum frequency at 6.1 GHz) with modulation and waveform generation capability; connected to a V950ME21-LF Voltage-Controlled Oscillator through a loop low filter, as shown in figure \ref{fig:sch_synth}. I found that the values of the components on the schematic were matching the ones on \textit{Clock 2} and \textit{Clock 3}, but were completely different for the \textit{Clock 1}. 

\begin{figure}[!h]
    \centering
    
    \captionsetup{justification=centering}
    \caption{Circuit schematic of demonstrator's synthesizer before repair.} 
    \label{fig:sch_synth}
\end{figure}

Due to the discrepancy in the component values, the components of the synthesizer circuit of \mbox{\textit{Clock 1}} were desoldered to be measured, obtaining the values of table \ref{table:components}.

\begin{table}[!h]
\centering
\begin{tabular}{|c|c|c|}
\hline
\textbf{Components}    & \textbf{Clock 1}           & \textbf{Clock 2, 3 and Schematic} \\ \hline
\textbf{R1}  & $5.1\; \mathrm{k\Omega}$ & $147\; \mathrm{\Omega}$        \\ \hline
\textbf{R2}  & $2.4\; \mathrm{k\Omega}$ & $83\; \mathrm{\Omega}$         \\ \hline
\textbf{R3}  & $4.7\; \mathrm{k\Omega}$ & $5.1 \mathrm{k\; \Omega}$      \\ \hline
\textbf{C14} & $330\; \mathrm{pF}$                     & $47\; \mathrm{nF}$                            \\ \hline
\textbf{C15} & $8.2\; \mathrm{nF}$                     & $680\; \mathrm{nF}$                           \\ \hline
\textbf{C16} & $680\; \mathrm{pF}$                     & $22\; \mathrm{nF}$                            \\ \hline
\end{tabular}
\caption{Loop filter components.}
\label{table:components}
\end{table}

After simulating the time and frequency domain behavior of the circuit in ADIsimPLL software (figure \ref{fig:simulation_1}), it was found that the loop bandwidth of the filter in \textit{Clock 2} and \textit{Clock 3} was 4.81 kHz, whereas, for the \textit{Clock 1} was 61.6 kHz. 

\begin{figure}[!h]
\centering
\begin{subfigure}[b]{\textwidth}
\centering

\captionsetup{justification=centering}
\caption{Phase Noise simulation of synthesizer loop filter \textit{Clock 2 and 3}.}
\end{subfigure}
\newline
\begin{subfigure}[b]{\textwidth}
\centering

\captionsetup{justification=centering}
\caption{Phase Noise simulation of synthesizer loop filter \textit{Clock 1}.}
\end{subfigure}
\caption{Comparison between synthesizer's Phase Noise simulation.} 
\label{fig:simulation_1}
\end{figure}

The loop bandwidth determines the frequency and phase lock time, lower values of loop bandwidth lead to reduced levels of phase noise and reference spurs, but at the expense of longer lock times and less phase margin.\cite{pll}

Indeed, the Time Domain simulation shows a lock time of approximately 1.5 ms for the \textit{Clock 2} and \textit{Clock 3}; and $25\; \mathrm{\mu s}$ for the \textit{Clock 1} (figure \ref{fig:time_simu}). 

\begin{figure}[!h]
\centering
\begin{subfigure}[b]{0.49\textwidth}
\centering

\captionsetup{justification=centering}
\caption{Lock Time simulation of synthesizer loop filter \textit{Clock 2 and 3}.}
\end{subfigure}
\hfill
\begin{subfigure}[b]{0.49\textwidth}
\centering

\captionsetup{justification=centering}
\caption{Lock Time simulation of synthesizer loop filter \textit{Clock 1}.}
\end{subfigure}
\caption{Comparison between synthesizer's Lock Time simulation.} 
\label{fig:time_simu}
\end{figure}

By replacing the components to match those of \textit{Clock 1} (figure\ref{fig:components_replacement}) it is now possible to have a 60 times faster lock time with a 12 times wider loop bandwidth.

\begin{figure}[!h]
    \centering
    
    \captionsetup{justification=centering}
    \caption{Replaced components based on \textit{Clock 1}.} 
    \label{fig:components_replacement}
\end{figure}

Finally, the components were replaced on synthesizer 2 and 3 and the circuits were tested on \mbox{\textit{Clock 1}} (as shown in figure \ref{fig:synth_final}), this solved the problem and now the three Atomic Clocks are operational and able to lock on the CPT transition.

\begin{figure}[!h]
\centering
\begin{subfigure}[b]{0.49\textwidth}
\centering

\captionsetup{justification=centering}
\caption{Synthesizer 2 - before.}
\end{subfigure}
\hfill
\begin{subfigure}[b]{0.49\textwidth}
\centering

\captionsetup{justification=centering}
\caption{Synthesizer 2 - after.}
\end{subfigure}
\newline
\centering
\begin{subfigure}[b]{0.49\textwidth}
\centering

\captionsetup{justification=centering}
\caption{Synthesizer 3 - before.}
\end{subfigure}
\hfill
\begin{subfigure}[b]{0.49\textwidth}
\centering

\captionsetup{justification=centering}
\caption{Synthesizer 3 - after.}
\end{subfigure}
\caption{Synthesizers 2 and 3 on \textit{Clock 1} before and after components replacement.} 
\label{fig:synth_final}
\end{figure}

\subsection{Recommendations}
It is worth pointing out the following recommendations for the clocks operation, as well as possible improvements that can be made to future versions of the software and hardware:

\begin{itemize}
    \item The best results in terms of stability were found when the middle absorption profile containing the CPT signal was positioned at 2.5 V or 2.6 V (by controlling the VCSEL temperature externally), since this is the middle of the ADC's measuring range.
    \item I recommend the ground terminal of the AC connector to be linked to the GND plane of the circuits, as this was found to be a considerable source of noise in the signal, specially when no instruments are connected to the demonstrator.
    \item I recommend the vapor cell of \textit{Clock 2} is replaced since the absorption signal was very weak, this leads to problems in locking both the laser and the quartz frequency. Furthermore, even though \textit{Clock 2} is now operational, it appears that the elements on the microwave section are disturbing and attenuating the signal.
    \item The larger the laser current scan range, the slower the refresh rate for the absorption graph becomes. This is due to the fact that a delay was added in the microcontroller code to make sure that the signal has the same period on the oscilloscope whether the data is being transmitted to the computer or not. To solve this limitation, and since the oscilloscope is no longer required, the delay can be removed on Arduino code (file: mac.ino, line: 686) for a faster response.
\end{itemize}

\subsection{Partial conclusion}
The improvements done in the CPT-based Cs microcell Atomic Clock pedagogical model are related to several aspects, like including a more intuitive and capable graphical user interface. For example, the controls are no longer in terms of machine units but in the respective physical unit. Also, there are now visual tools to have a precise value of the maximum absorption point and the locking current and frequency. Additionally, I was able to fix two of the Atomic Clocks that were not working properly by analyzing and modifying their Phase lock loop synthesizer circuits. The improvements added to this project are very significant compared to the previous version. 
\section{Final conclusion}
The two projects that are part of my Master 1 internship are the "Superradiant laser instrumentation process" and "Improvements on CPT-based Cs microcell Atomic Clock
pedagogical model". The former project included the implementation of a robust communication protocol between the instrumentation elements in the laboratory, that was previously erratic. Also, another significant contribution for this project was the addition of a standalone single board computer (LattePanda) to run the wavelength meter software and UDP server written in C++. 

As for the second project, it is related to the atomic clock used in yearly EFTS, which required plenty of improvements to work in a satisfactory and reliable manner. This will allow the attendees of EFTS to have the opportunity to focus on the theory behind the atomic clock, instead of focusing too much on how to control the elements in a non-intuitive manner. %As future improvements, the ground from the outlet should be connected to the atomic clock circuit ground. This would solve the problem of having a high level of noise when no instruments are connected. And also the Atomic \textit{Clock 2} signal can be improved, even though it's now operational, it appears that the elements on the microwave section are disturbing and attenuating the signal.
%References:
\section{Acknowledgment}
I gratefully thank Dr. Marion DELEHAYE, Dr. Rodolphe BOUDOT and Dr. Jean-Michel FRIEDT for their help and time to guide me in both projects.
% \newpage
\bibliographystyle{unsrt} % We choose the "plain" reference style
\bibliography{refs} % Entries are in the refs.bib file

\end{document}

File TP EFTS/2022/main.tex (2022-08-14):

\documentclass[a4paper,11pt]{article}
\usepackage[utf8]{inputenc}
\usepackage[T1]{fontenc}
\usepackage[normalem]{ulem}
\usepackage[english]{babel}
\usepackage{verbatim}
\usepackage{graphicx}
\usepackage{color} % définit une nouvelle couleur
\usepackage{float}
\usepackage[a4paper]{geometry}
\usepackage{hyperref}
\usepackage{bm, mathtools,amsmath, amssymb,upgreek}
\usepackage{tikz}
\geometry{hscale=0.8,vscale=0.8,centering}
%CR:
\usepackage{caption}

\newcounter{manip}
\newenvironment{manip}[1][]{\refstepcounter{manip}\par\medskip
	\textbf{Manipulation~\themanip. #1} \rmfamily }{\medskip}

\newcounter{question}
\newenvironment{question}[1][]{\refstepcounter{question}\par\medskip
	\textbf{Question~\thequestion. #1} \rmfamily }{\medskip}

\definecolor{QuestionColor}{rgb}{0.9,0.95,1} % bleu ciel
\definecolor{SolutionColor}{rgb}{0.9,0.95,1} % bleu ciel

\newcommand{\be}{\begin{equation}}
\newcommand{\ee}{\end{equation}}
\newcommand{\bea}{\begin{eqnarray}}
\newcommand{\eea}{\end{eqnarray}}
\newcommand{\MI}{|\rm{MI}\rangle}
\newcommand{\SF}{|\rm{SF}\rangle}
\newcommand{\ah}{\hat{a}}
\newcommand{\ac}{\hat{a}^\dag}

\title{Lab Work \\ CPT-based Cs microcell atomic clock}
\author{}
\date{2022}
\begin{document}
\maketitle

\tableofcontents 

\section{Basics on miniature atomic clocks}
Figure \ref{fig:globalcpt} shows the architecture of a miniature Cs cell atomic clock based on coherent population trapping (CPT).

\begin{figure}[h!]
	\centering
	
	\caption{Simplified architecture of a buffer-gas filled Cs microcell CPT atomic clock.}
	\label{fig:globalcpt}
\end{figure}

Cs vapor is filled in a glass-silicon-glass micro-fabricated cell whose technology is described in~\cite{hasegawa}. The Cs cell is filled with a pressure buffer gas. The buffer gas slows down atoms in the microcell and increases the time for the atoms to reach the cell walls. It also reduces the first-order Doppler effect and leads to operation in the Lamb-Dicke regime~\cite{dicke}. Eventually, it helps to detect narrow CPT resonances.

Atoms in the cell interact with a dual-frequency (in the ideal case!) optical field generated by a VCSEL laser whose injection current is directly modulated at 4.596 GHz through a bias-tee. This generates two first-order optical sidebands separated by about 9.192 GHz, required to produce the CPT interaction. The laser output beam crosses a neutral density filter to attenuate the optical power and a quarter-wave plate to polarize circularly the optical beam. The light transmitted through the cell is detected by a photodiode.

When the frequency difference between both first-order optical sidebands exactly equals the Cs ground-state hyperfine splitting (9.192 631 770 GHz), atoms are trapped through a quantum interference process in a quantum superposition of both ground states (see Fig.~\ref{fig:ppeCPT}). In this so-called dark state, the light atomic absorption is reduced and the atomic vapor transparency is increased. The CPT resonance linewidth is ultimately limited by the microwave CPT coherence relaxation time and can be measured to be of about 1 kHz in a buffer-gas filled micro-fabricated cell. The signal at the output of the photodiode is used in two main servo loops. The first one is dedicated to the stabilization of the laser frequency onto the bottom of a homogeneously broadened optical line. The second loop stabilizes the local oscillator (LO) frequency onto the atomic clock transition.

\begin{figure}[h!]
	\centering
	
	\caption{Basic principle of CPT.}
	\label{fig:ppeCPT}
\end{figure}

\section{Presentation of the CPT clock experiment}
Figure~\ref{fig:environnement} shows the table-top experiment environment. The oscilloscope was used to monitor the output of the photodiode, but it is not needed any more since the monitoring is now done in the software.

\begin{figure}[h!]
	\centering
	
	\caption{Table-top CPT experiment environment. From left to right: personal computer to pilot the experiment, 		oscilloscope to monitor signals, the CPT clock card including physics package and all embedded electronics, a Thorlabs 		TEC200C controller used to stabilize the VCSEL temperature. On the top-right, a power-supply to drive the clock-card, 		a frequency counter (HP53132A), a spectrum analyzer used to monitor the local oscillator microwave signal at 4.6 GHz 		and a Symmetricom 5125A test-set to measure the clock Allan deviation. A hydrogen maser 10 MHz signal cable is also 		available.}
	\label{fig:environnement}
\end{figure}

Figure~\ref{fig:clock-card} shows a zoom on the clock-card that is now inside the clock case.

\begin{figure}[h!]
	\centering
	
	\caption{Details of the clock-card.}
	\label{fig:clock-card}
\end{figure}

{\bf Important points: }

VCSEL : 894.6 nm (Cs D1 line);
Microcell: Cs-Ne ($\approx 76$~Torr), heated at about 75$^\circ$C. The cell length is 1.4~mm. Its diameter is 2~mm.
The static magnetic field applied along the cell can be tuned using a current value. It is applied in order to lift the Zeeman degeneracy. 

Figure~\ref{fig:gui} shows the typical interface program window to pilot the clock. A C program was implemented to pilot a microcontroller through an Arduino platform. An upgraded python interface has been developed this year. We have done our best to make it as stable as possible but it is the first time it is tested live, so please report any bug.%A preliminary Python interface was developed to operate the clock. You can visualize the commands and digital words sent to the micro-controller at any time in the command window.

\begin{figure}[h!]
	\centering
	
	\caption{Program graphic interface.}
	\label{fig:gui}
\end{figure}

The program is launched from a Jupyter Notebook which should be already running on your labwork computer.

\section{Lab work}
%\subsection{Open the main program interface}
%!!! CARLOS please check this subsection !!!
%The graphical interface is ran from a jupyter notebook which will be already running when you start the labwork. 

%In case you need to restart the interface, simply chose the “Restart and Clear Output” under the “Kernel” menu, and re-run the first cell of the notebook.

%With the Jupyter Notebook, you can execute code and/or plot your data in the same session.

\subsection{Initial configuration}
The laser temperature set-point has been pre-set using the Thorlabs TED200C. It is set at 75$^\circ$C (1.609 k$\Omega$) for the clock 1, around 80$^\circ$C (1.206 k$\Omega$) for the clock 2 and around 70$^\circ$C (1.866 k$\Omega$) for the clock 3 .
For the first step, the 4.6 GHz signal power is turned off by the microwave attenuator at the output of the local oscillator card (the sliders 1 to 6 are set to “1”, see Fig.~\ref{fig:attenuation}). The microwave attenuator is accessible on the side on the clock case.
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


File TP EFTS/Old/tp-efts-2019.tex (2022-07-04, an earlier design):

\documentclass[a4paper,11pt]{article}
\usepackage[utf8]{inputenc}
\usepackage[T1]{fontenc}
\usepackage[normalem]{ulem}
\usepackage[english]{babel}
\usepackage{verbatim}
\usepackage{graphicx}
\usepackage{color} % définit une nouvelle couleur
\usepackage{float}
\usepackage[a4paper]{geometry}
\usepackage{hyperref}
\usepackage{bm, mathtools,amsmath, amssymb,upgreek}
\usepackage{tikz}
\geometry{hscale=0.8,vscale=0.8,centering}

\newcounter{manip}
\newenvironment{manip}[1][]{\refstepcounter{manip}\par\medskip
	\textbf{Manipulation~\themanip. #1} \rmfamily }{\medskip}
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

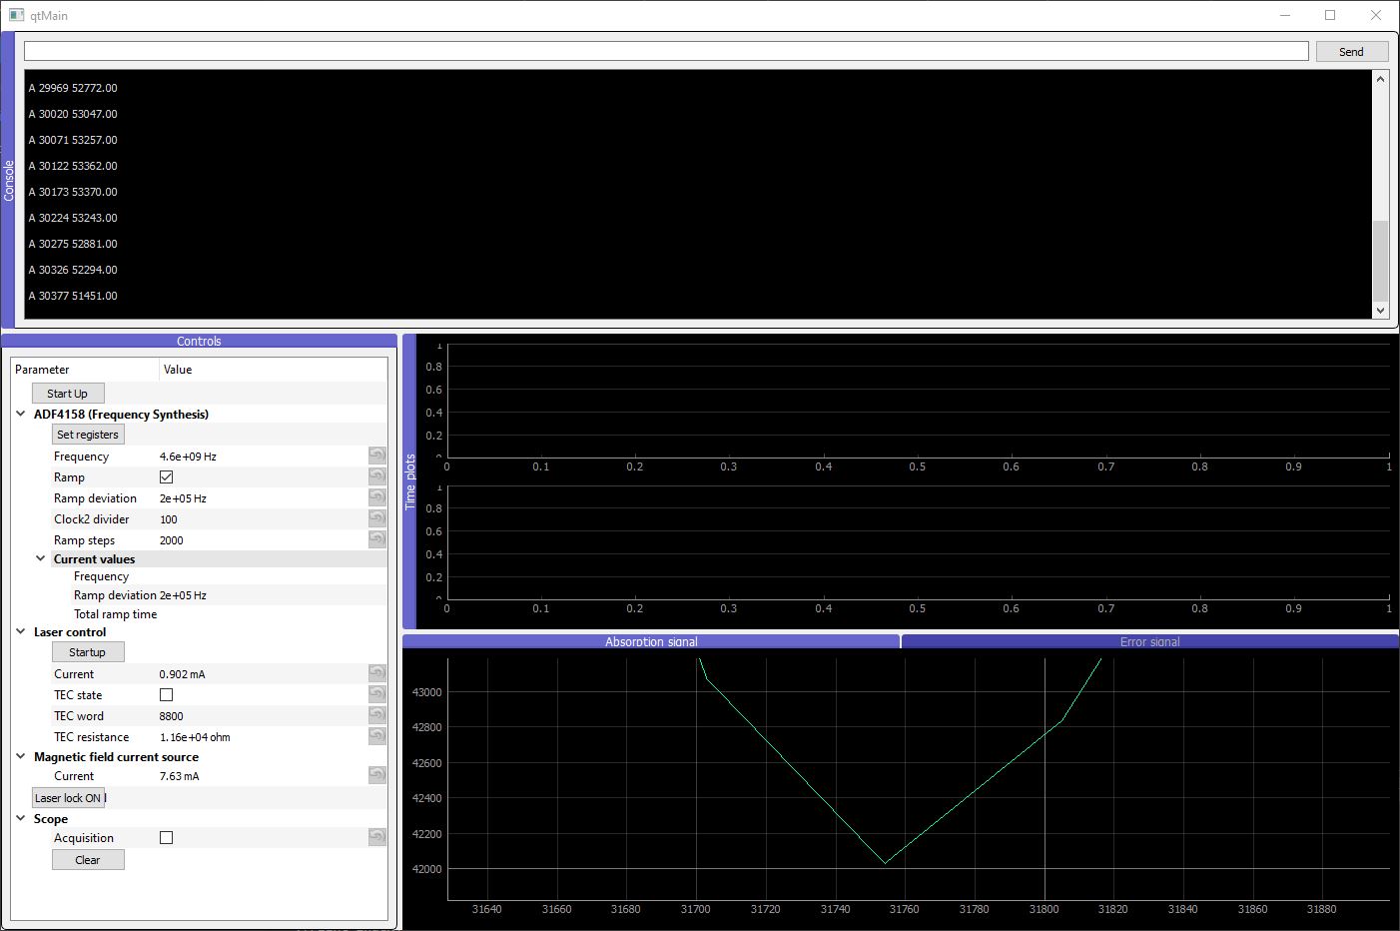
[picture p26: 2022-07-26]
Screen captures/CPT Spectrum zoom.JPG

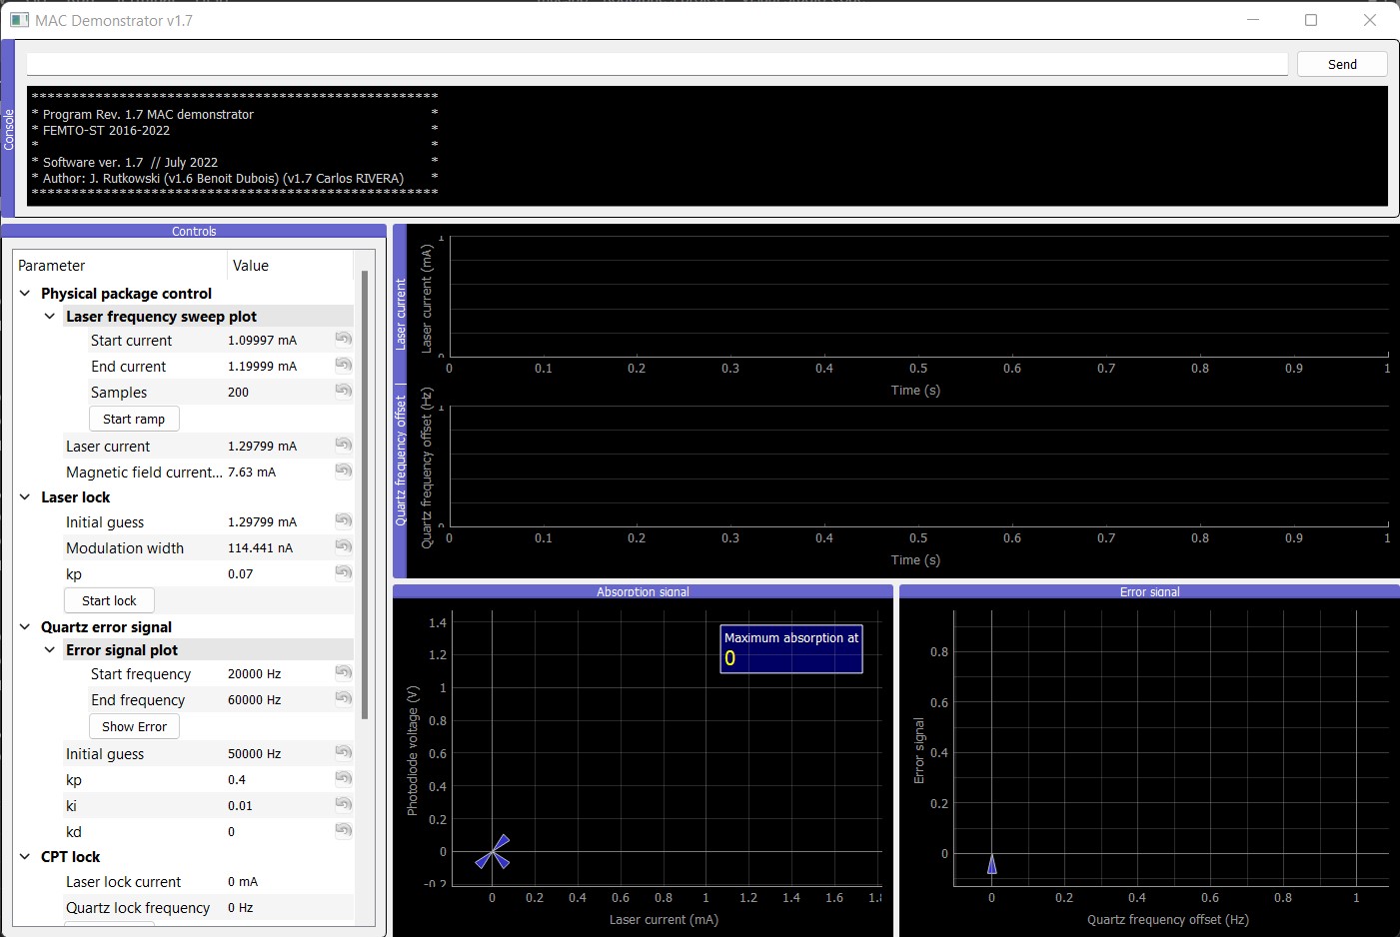
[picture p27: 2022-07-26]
Screen captures/For EFTS report/Captura de pantalla 2022-07-04 183317.jpg

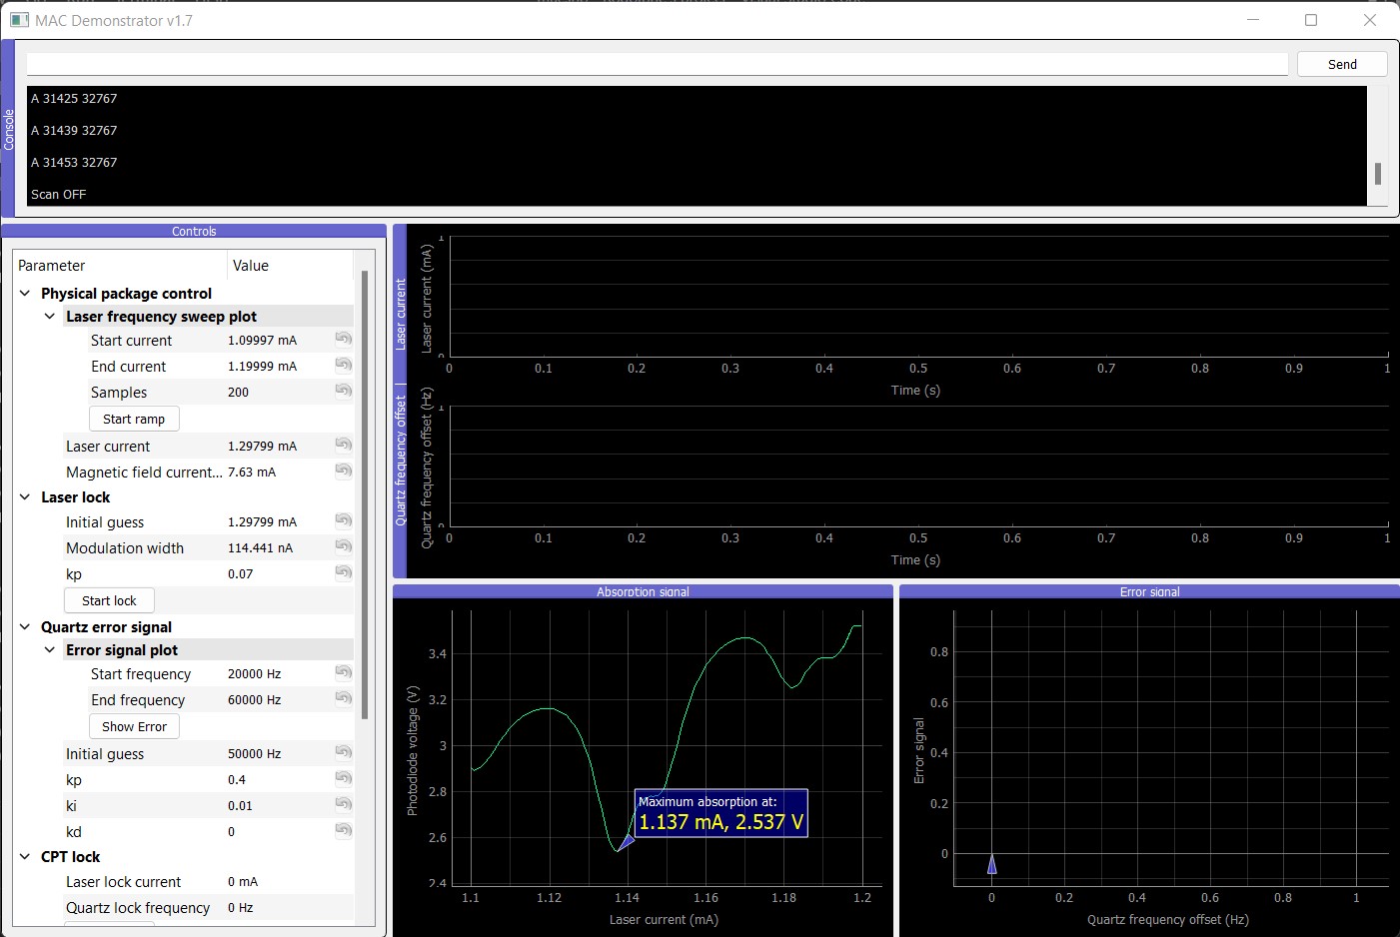
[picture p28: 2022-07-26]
Screen captures/For EFTS report/Captura de pantalla 2022-07-04 182409.jpg

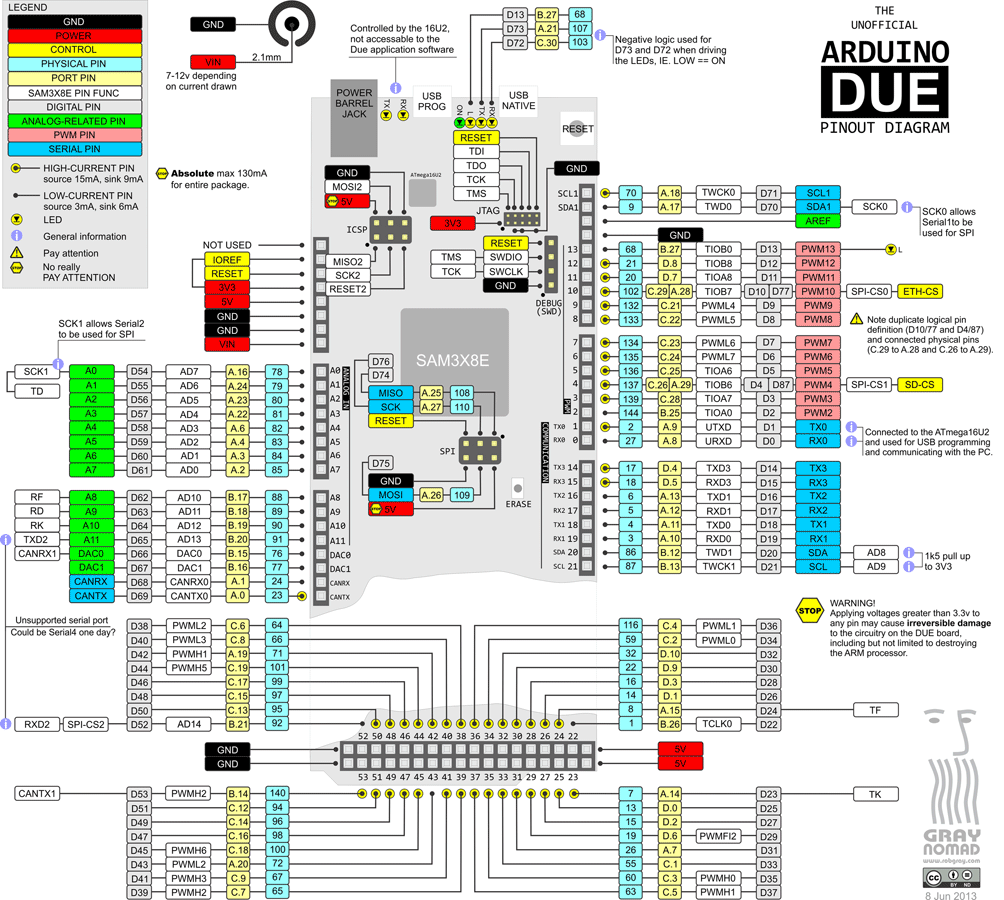
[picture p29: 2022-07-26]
Documentation/Datasheets/Arduino_DUE_pinout.png

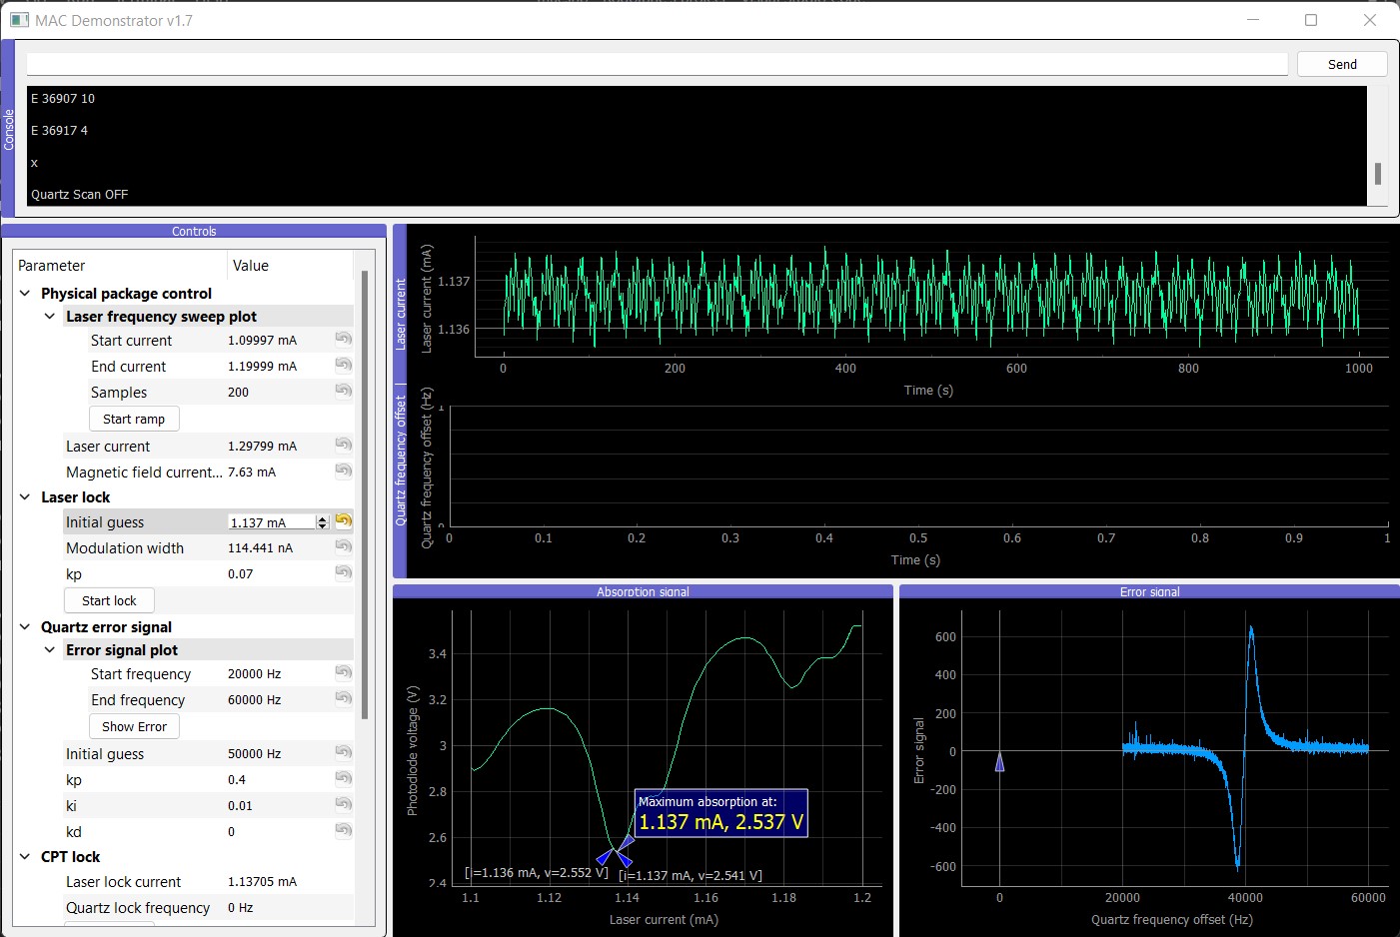
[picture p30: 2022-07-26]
Screen captures/For EFTS report/Captura de pantalla 2022-07-04 182453.jpg

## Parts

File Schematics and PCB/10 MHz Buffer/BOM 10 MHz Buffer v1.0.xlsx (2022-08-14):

Bill of Materials
Assembly Name: | 10 MHz Buffer
Revision: | 1.0
Date: | 2016-06-22
Part Name | Value | Package | Description | Manufacturer | MPN | Ref. Farnell | Quantity | Approx. Unit Price | Stock
C1, C2, C3, C5, C6, C7 | 0,1 u | 0603 | Condensateur céramique multicouche CMS, 0.1 µF, ± 10%, X7R, 50 V, 0603 [1608 Metric] | WALSIN | 0603B104K500CT | 2496834 | 6 | 0.0126 | ok
C4 | 10 u | 0805 | Condensateur céramique multicouche CMS, Série GRM, 10 µF, ± 10%, X5R, 25 V, 0805 [2012 Metric] | MURATA | GRM219R61E106KA12D | 2426961 | 1 | 0.129 | ok
R1 | 200 | 0603 | Resistor 200 ohm, generic | - | - | - | 1 | - | ok
R2 | 49.9 | 0603 | Resistor 49,9 ohm, generic | - | - | - | 1 | - | ok
IN, OUT | - | U.FL | Connecteur coaxial / RF, Coaxial RF, Jack droit, Montage en surface vertical, 50 ohm, Laiton | MOLEX | 73412-0110 | 1340200 | 2 | 0.784 | ok
JP1 | - | THT (2,54 mm) | Pin header 1x2, VCC, generic | - | - | - | 1 | - | ok
IC1 | - | VSSOP-8 | Buffer, Non-Inverseur, 800mV à 3.6V | TEXAS INSTRUMENTS | SN74AUP2G241DCUR | 1813459 | 1 | 0.309 | none
IC2 | - | SOIC-8 | Régulateur LDO Tension fixe, 3.2V à 12V, 180mV Dropout, 3.3Vout, 200mAout, SOIC-8 | ANALOG DEVICES | ADP3303ARZ-3.3 | 2305721 | 1 | 2.53 | ok
IC3 | - | SOT-23-5 | Porte Logique Inverseur, Ultra rapide, 1 entrée, 32 mA, 1.65V à 5.5V | FAIRCHILD SEMICONDUCTOR | NC7SZ04M5X | 1417667 | 1 | 0.593 | none

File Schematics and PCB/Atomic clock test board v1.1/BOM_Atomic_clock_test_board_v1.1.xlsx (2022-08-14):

Bill of Materials
Assembly Name: | Atomic clock test board
Revision: | 1.1
Date: | 2016-06-16
Part Name | Value | Package | Description | Manufacturer | MPN | Ref. Farnell | Quantity | Approx. Unit Price | Stock
C1, C4, C7, C13 | 1u | 0603 | Condensateur céramique multicouche CMS, Série GRM, 1 µF, ± 10%, X5R, 6.3 V | MURATA | GRM188R60J105KA01D | 9527699 | 4 | 0.0314 | ok
C2, C3, C8, C9, C10, C11 | 0.1u | 0603 | Condensateur céramique multicouche CMS, 0.1 µF, ± 10%, X7R, 50 V, 0603 [1608 Metric] | WALSIN | 0603B104K500CT | 2496834 | 6 | 0.0126 | ok
C5, C6, C12 | 10 u | 0603 | Condensateur céramique multicouche CMS, Série ZRA, 10 µF, ± 20%, X5R, 25 V | MURATA | ZRB18AR61E106ME01L | 2469398 | 3 | 0.28 | none
R1 | 200 | 0603 | Résistance CMS, Couche mince, Série PCF, 200 ohm, 63 mW, ± 0.1%, 50 V | WELWYN | PCF0603R-200RBT1 | 1353134 | 1 | 0.434 | none
R2, R4 | 100 | 0603 | Résistance CMS, Couche mince, Série PCF, 100 ohm, 63 mW, ± 0.1%, 50 V | WELWYN | PCF0603R-100RBT1 | 1160304 | 2 | 0.434 | none
R3 | 10 | 0603 | Résistance CMS, Couche mince, Série WIN, 10 ohm, 100 mW, ± 0.1%, 75 V | WELWYN | WINT0603LF0310R0B | 2428787 | 1 | 0.773 | none
R5, R6, R7, R8, R9, R10 | 330 | 0603 | Résistance CMS, Couche épaisse, Série MCWR, 330 ohm, 100 mW, ± 1%, 50 V | MULTICOMP | MCWR06X3300FTL | 2447339 | 6 | 0.0067 | ok
ADC_CON | - | THT | Connecteur carte-à-carte, Vertical, Série Archer M52, 5 Contact(s), Embase, 1.27 mm | HARWIN | M52-5000545 | 1099543 | 1 | 0.541 | none
SUPPLY | - | THT | Bornier fil-à-carte, 2 Voies, 300 V, 16 A, 26 AWG, 12 AWG | MULTICOMP | MC000048 | 2008019 | 1 | 0.406 | none
SYNTHESIZER, TEC_CONTROLLER, CELL_TEMP_CONTR | - | SMD | Connecteur fil-à-carte, Série PicoBlade 53398, 8 Contact(s), Embase, 1.25 mm | MOLEX | 53398-0871 | 1125371 | 3 | 1.43 | none
CELL_TEMP_SUBD | - | THT | Connecteur Sub D standard, Angle Droit, Série 182, DE, Embase, 9, Corps en acier | NORCOMP | 182-009-213R171 | 2294287 | 1 | 1.79 | ok
TEC_SUB-D | - | THT | Connecteur Sub D standard, Série SD, DE, Mâle, 9, Corps en acier | AMPHENOL | L717SDE09P1ACH4F | 2401240 | 1 | 3.28 | ok
CON1 | - | IDC THT | Connecteur fil-à-carte, Vertical, Série T821, 20 Contact(s), Embase, 2.54 mm | AMPHENOL | T821120A1S100CEU | 2215309 | 1 | 0.533 | ok
MUXOUT, PD_SIGNAL, ILD_EXT | - | U.FL | Connecteur coaxial / RF, Coaxial RF, Jack droit, Montage en surface vertical, 50 ohm, Laiton | MOLEX | 73412-0110 | 1340200 | 3 | 0.784 | none
IC1, IC2 | - | TSOT23-5 | Amplificateur opérationnel, Simple, 400 kHz, 1 amplificateur, 0.1 V/µs, 1.8V à 5V | ANALOG DEVICES | AD8603AUJZ | 1651290 | 2 | 2.01 | none
T1 | - | SOT23 | Transistor simple bipolaire (BJT), NPN, 40 V, 300 MHz, 300 mW, 200 mA, 100 hFE | DIODES INC. | MMBT3904-7-F | 1773602 | 1 | 0.0726 | none
U$2, U$4 | - | MSOP-8 | Amplificateur différentiel, Niveau Adaptateur, 1 Amplificateur(s), 300 µV, 15 MHz, -40 °C, 85 °C | ANALOG DEVICES | AD8275ARMZ | 2094193 | 2 | 3.78 | ok
U$5 | - | SOIC-8 | Régulateur LDO Tension fixe, 4.5V à 16V, 600mV Dropout, 5Vout, 800mAout | ANALOG DEVICES | ADM7150ARDZ-5.0 | 2377358 | 1 | 7.37 | none
U1,U2 | - | SOIC-8 | Convertisseur numérique vers analogique, 16 bit, Série, 2.7V à 5.5V | LINEAR TECHNOLOGY | LTC1655LIS8#PBF | 2294807 | 2 | 17.06 | none

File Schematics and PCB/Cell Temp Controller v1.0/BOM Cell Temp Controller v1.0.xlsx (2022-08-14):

Bill of Materials
Assembly Name: | Cell Temp Controller
Revision: | 1.0
Date: | 2016-06-16
Part Name | Value | Package | Description | Manufacturer | MPN | Ref. Farnell | Quantity | Approx. Unit Price
C5, C8, C12, C13, C14, C15, C16, C17 | 0,1 u | 0603 | Condensateur céramique multicouche CMS, 0.1 µF, ± 10%, X7R, 50 V | WALSIN | 0603B104K500CT | 2496834 | 9 | 0.0126
C3, C4 | 22 p | 0603 | Condensateur céramique multicouche CMS, Série C, 22 pF, ± 5%, C0G / NP0, 50 V | TDK | C1608C0G1H220J080AA | 1907288 | 2 | 0.0169
C2, C6, C9 | 1 u | 0603 | Condensateur céramique multicouche CMS, Série GRM, 1 µF, ± 10%, X5R, 6.3 V | MURATA | GRM188R60J105KA01D | 9527699 | 3 | 0.0314
C1, C10, C7, C11 | 10 u | 0603 | Condensateur céramique multicouche CMS, Série ZRA, 10 µF, ± 20%, X5R, 25 V | MURATA | ZRB18AR61E106ME01L | 2469398 | 4 | 0.28
R1, R2 | 22 | 0603 | Résistance à puce CMS, Couche épaisse, Série MC, 22 ohm, 50 V | MULTICOMP | MC0063W0603522R | 9331891 | 2 | 0.0096
R3 | 1 M | 0603 | Résistance CMS, Couche mince, Série MCT, 1 Mohm, 100 mW, ± 1%, 75 V | VISHAY | MCT06030C1004FP500 | 2325293 | 1 | 0.206
R4, R5 | 10 k | 0603 | Résistance CMS, Céramique, Série MCMR, 10 kohm, 100 mW, ± 1%, 75 V | MULTICOMP | MCMR06X1002FTL | 2073349 | 2 | 0.0149
R7, R8, R9 | 10 k 0,1% | 0603 | Résistance CMS, Couche métallique, Série AEC-Q200 ERA, 10 kohm, 100 mW, ± 0.1%, 150 V | PANASONIC ELECTRONIC COMPONENTS | ERA3ARB103V | 1717597 | 3 | 1.21
R11 | 13 | 2010 | Résistance CMS, Couche épaisse, Série MCPWR, 13 ohm, 750 mW, ± 1%, 400 V | MULTICOMP | MCPWR10FTFQ0130 | 1887569 | 1 | 0.34
D1, D2 | - | SOD-123 | Diode de récupération standard, Une, 400 V, 700 mA, 980 mV, 150 A | ROHM | RR255M-400TR | 1525525 | 2 | 0.305 | Older--> 1525524
F1 | - | 1812 | FUSIBLE POLYSWITCH CMS 0.5A | TE CONNECTIVITY / RAYCHEM | MINISMDC050F-2 | 1175839 | 1 | 0.391
V1, V2 | - | 0603 | Varistance TVS, AEC-Q200 ChipGuard MLC Series, 8 V, 5 V, 20 V | BOURNS | CG0603MLC-05E | 1838966 | 2 | 0.134
ICSP | - | THT (2,54) | Connecteur carte-à-carte, Vertical, Série AMPMODU Mod II, 6 Contact(s), Embase, 2.54 mm | TE CONNECTIVITY / AMP | 826925-3 | 1248132 | 1 | 0.272
SUPPLY | - | THT (2,54) | Connecteur carte-à-carte, Série KK 4030, 3 Contact(s), Embase, 2.54 mm, Traversant, 1 Rangée(s) | MOLEX | 2031-03-22 | 9731083 | 1 | 0.148
SW1 | - | SMD | Commutateur tactile, Non lumineux, 1.5 N, 12 V, 50 mA, A souder | OMRON ELECTRONIC COMPONENTS | B3U-1000P | 1333652 | 1 | 0.768
TH_SIG | - | U.FL | Connecteur coaxial / RF, Coaxial RF, Jack droit, Montage en surface vertical, 50 ohm, Laiton | MOLEX | 73412-0110 | 1340200 | 1 | 0.784
USB | - | SMD | Connecteur USB, Micro USB Type B, USB 2.0, Embase, 5 Voies | MOLEX | 47346-0001 | 1568026 | 1 | 0.9
ANALOG_I/O | - | THT | Connecteur Sub D standard, Série SD, DE, Mâle, 9, Corps en acier | AMPHENOL | L717SDE09P1ACH4F | 2401240 | 1 | 3.28
Q1 | - | SMD (CX2520SB) | CRYSTAL, SM, 16MHZ, 2.5X2.0 | AVX | CX2520SB16000D0FLJZZ | 1657886 | 1 | 2.77
U$1 | - | SOIC-8 | Régulateur LDO Tension fixe, 4.5V à 16V, 600mV Dropout, 5Vout, 800mAout | ANALOG DEVICES | ADM7150ARDZ-5.0 | 2377358 | 1 | 7.37
U$2 | - | SOT-223 | SOURCE DE COURANT PROGR. 0.2A | LINEAR TECHNOLOGY | LT3092EST#PBF | 2295469 | 1 | 3.79
IC1 | - | TSOT23-5 | Amplificateur opérationnel, Simple, 400 kHz, 1 amplificateur, 0.1 V/µs, 1.8V à 5V | ANALOG DEVICES | AD8603AUJZ | 1651290 | 1 | 2.01
U1 | - | TQFP-44 | ATMEGA32U4-AU MICRO 8 BITS AVR 32K FLASH USB | ATMEL | ATMEGA32U4-AU | 1748525 | 1 | 5.2
U3 | - | MSOP-12 | Ultra-Tiny, 16-Bit ΔΣ ADC with 10ppm/°C Max Precision Reference | LINEAR TECHNOLOGY | LTC2462IMS#PBF | LT, Digi-Key, Conrad | 1 | 3.65
U4 | - | SOIC-8 | Convertisseur numérique vers analogique, 16 bit, Série, 2.7V à 5.5V | LINEAR TECHNOLOGY | LTC1655LIS8#PBF | 2294807 | 1 | 17.06

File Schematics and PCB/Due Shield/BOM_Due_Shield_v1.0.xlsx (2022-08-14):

Bill of Materials
Assembly Name: | Due Shield
Revision: | 1.0
Date: | 2016-08-19
Part Name | Value | Package | Description | Manufacturer | MPN | Ref. Farnell | Quantity | Approx. Unit Price | Stock
C1, C2 | 1u | 0805 | Condensateur céramique multicouche CMS, Série GRM, 1 µF, ± 10%, X7R, 50 V | MURATA | GRM21BR71H105KA12L | 1735541 | 2 | 0.158 | none
C3 | 0.1u | 0805 | Condensateur céramique multicouche CMS, Série GRM, 0.1 µF, ± 10%, X7R, 50 V | MURATA | GRM21BR71H104KA01L | 8820120 | 1 | 0.0874 | none
R1 | 10k | 0603 | Résistance à puce CMS, Céramique, Série MCMR , 10 kohm, 75 V, 100 mW, ± 1% | MULTICOMP | MCMR06X1002FTL | 2073349 | 1 | 0.0142 | ok
R2 | 750k | 0603 | Résistance à puce CMS, Couche mince, Série MCT, 750 kohm, 75 V,100 mW, ± 1% | VISHAY | MCT06030C7503FP500 | 2325290 | 1 | 0.122 | none
R3, R4 | 62k | 0603 | Résistance à puce CMS, Couche épaisse, Série AEC-Q200 CRCW, 62 kohm, 75 V | VISHAY | CRCW060362K0FKEA | 2138478 | 2 | 0.0147 | none
R6, R7 | 100k | 0603 | Résistance à puce CMS, Couche épaisse, Série RC, 100 kohm, 50 V, 100 mW, ± 1% | YAGEO | RC0603FR-13100KL | 2309107 | 2 | 0.0195 | ok
CON1 | - | IDC THT | Connecteur fil-à-carte, Vertical, Série T821, 20 Contact(s), Embase, 2.54 mm | AMPHENOL | T821120A1S100CEU | 2215309 | 1 | 0.533 | ok
BOARD_SUPP | - | THT | Bornier fil-à-carte, 2 Voies, 300 V, 16 A, 26 AWG, 12 AWG | MULTICOMP | MC000048 | 2008019 | 1 | 0.406 | ok
POWER_JACK | - | THT | Connecteur d'alimentation DC, Femelle, 5 A, 2.5 mm | CLIFF ELECTRONIC COMPONENTS | FC681465P | 1854512 | 1 | 1.24 | none
SW1 | - | THT | Commutateur à glissière, Série 1000, SPDT, On-Aucun-On, 6 A, 250 V | C & K COMPONENTS | 1101M2S3CQE2 | 1437697 | 1 | 3.26 | none
U$1 | - | THT | Commutateur tactile, Non lumineux, 1.57 N, 24 V, 50 mA, A souder | OMRON ELECTRONIC COMPONENTS | B3W-1000 | 176986 | 1 | 0.448 | none
X1, X2 | - | THT | Connecteur coaxial / RF, Coaxial SMA, Jack droit, A souder, Laiton | TE CONNECTIVITY / GREENPAR | 1-1478979-0 | 1056377 | 2 | 4.62 | none
U$2 | - | SOIC-8 | Régulateur de tension LDO, Ajustable, 3.3V à 20V in, 350mV drop, 1.22V à 19V/0.5A out | ANALOG DEVICES | ADP7105ARDZ | 2361533 | 1 | 3.89 | none

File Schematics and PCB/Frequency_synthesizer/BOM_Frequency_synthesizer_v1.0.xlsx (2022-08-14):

Bill of Materials
Assembly Name: | Frequency synthesizer
Revision: | 1.0
Date: | 2016-05-03
Part Name | Value | Package | Description | Manufacturer | MPN | Ref. Farnell | Quantity | Approx. Unit Price
C1, C2, C3, C6, C7, C8, C9, C12, C22 | 0.1u | 0603 | Condensateur céramique multicouche CMS, 0.1 µF, ± 10%, X7R, 50 V, 0603 [1608 Metric] | WALSIN | 0603B104K500CT | 2496834 | 9 | 0.0126
C4 | 10u | 0805 | Condensateur céramique multicouche CMS, Série GRM, 10 µF, ± 10%, X5R, 25 V, 0805 [2012 Metric] | MURATA | GRM219R61E106KA12D | 2426961 | 1 | 0.129
C5 | 0.33u | 0603 | Condensateur céramique multicouche CMS, Série C, 0.33 µF, ± 10%, X5R, 25 V, 0603 [1608 Metric] | TDK | C1608X5R1E334K080AC | 2346893 | 1 | 0.0822
C10, C11, C18, C23 | 10p | 0603 | Condensateur céramique multicouche CMS, Série MC, 10 pF, ± 0.5pF, C0G / NP0, 50 V | MULTICOMP | MC0603N100D500CT | 1759053 | 3 | 0.0248
C13, C19, C20, C21 | 100p | 0402 | CONDENSATEUR RF NP0 100PF 50V 0402 | MULTICOMP | MCHH15N101J500CT | 2310297 | 4 | 0.0046
C14 | 47n | 0602 | Condensateur céramique multicouche CMS, 0.047 µF, ± 5%, X7R, 25 V, 0603 [1608 Metric] | WALSIN | 0603B473J250CT | 2496864 | 1 | 0.0177
C15 | 0.68u | 0603 | Condensateur céramique multicouche CMS, Série MC, 0.68 µF, ± 10%, X5R, 16 V, 0603 [1608 Metric] | MULTICOMP | MC0603X684K160CT | 1759406 | 1 | 0.0706
C16 | 22n | 0603 | Condensateur céramique multicouche CMS, 0.022 µF, ± 5%, X7R, 50 V, 0603 [1608 Metric] | AVX | 06035C223JAT2A | 2332645 | 1 | 0.376
C17 | 22u | 0805 | Condensateur céramique multicouche CMS, Série GRM, 22 µF, ± 20%, X5R, 25 V, 0805 [2012 Metric] | MURATA | GRM21BR61E226ME44L | 1907510 | 1 | 0.504
R1 | 147 | 0603 | Résistance CMS, Couche mince, Série WIN, 147 ohm, 100 mW, ± 0.1%, 75 V, 0603 [1608 Metric] | WELWYN | WINT0603LF031470B | 2428794 | 1 | 0.774
R2 | 71.5 | 0603 | Résistance CMS, Couche mince, Série CPF, 71.5 ohm, 63 mW, ± 0.1%, 50 V, 0603 [1608 Metric] | TE CONNECTIVITY | CPF0603B71R5E1 | 2331358 | 1 | 0.686
R3 | 5k1 | 0603 | Résistance CMS, Couche mince, Série PCF, 5.1 kohm, 63 mW, ± 0.1%, 50 V, 0603 [1608 Metric] | WELWYN | PCF0603P-R-5K1-BT1 | 1506015 | 1 | 0.44
R4, R5, R6, R8 | 330 | 0603 | Résistance CMS, Couche épaisse, Série MCWR, 330 ohm, 100 mW, ± 1%, 50 V, 0603 [1608 Metric] | MULTICOMP | MCWR06X3300FTL | 2447339 | 4 | 0.0067
R10, R11, R12 | 18 | 0402 | Résistance CMS, Couche mince, Série CPF, 18 ohm, 63 mW, ± 0.1%, 25 V, 0402 [1005 Metric] | TE CONNECTIVITY / NEOHM | CPF0402B18RE1 | 1697295 | 3 | 0.711
R13 | 50 | 0402 | RESISTANCE MICROWAVE 50R 0402 | VISHAY | FC0402E50R0BSWS | 1109049 | 1 | 3.28
I/O | - | 53398-08 | Connecteur fil-à-carte, Série PicoBlade 53398, Montage CMS, Embase, 8, 1.25 mm | MOLEX | 53398-0871 | 1125371 | 1 | 1.43
10MHZ_OUT, TXDATA_IN | - | U.FL | Connecteur coaxial / RF, Coaxial RF, Jack droit, Montage en surface vertical, 50 ohm, Laiton | MOLEX | 73412-0110 | 1340200 | 2 | 0.784
RF_OUT | - | SMA | Connecteur coaxial / RF, Coaxial SMA, Jack droit, A souder, 50 ohm, Cuivre-béryllium | JOHNSON | 142-0701-851 | 1019325 | 1 | 4.97
TCXO | - | TCXO-CFPT-126 | OSCILLATEUR A QUARTZ CMS 10MHZ | IQD FREQUENCY PRODUCTS | LFTVXO009912 | 1100747 | 1 | 26.83
U$1 | - | SOT-223 | Linear Voltage Regulator, Fixed, 7V To 25V In, 5V And 0.5A Out | TEXAS INSTRUMENTS | UA78M05QDCYRG4Q1 | 2383041 | 1 | 0.718
U1 | - | LFCSP-24 | SYNTHETISEUR FREQUENCE 6.1GHZ LFCSP-24 | ANALOG DEVICES | ADF4158CCPZ | 2377117 | 1 | 9.94
U2 | - | SOIC-8 | Convertisseur numérique vers analogique, 16 bit, Série, 2.7V à 5.5V, SOIC, 8 | LINEAR TECHNOLOGY | LTC1655LIS8#PBF | 2294807 | 1 | 19.1
U3 | - | SOIC-8 | Régulateur LDO Tension fixe, 3.2V à 12V, 180mV Dropout, 3.3Vout, 200mAout, SOIC-8 | ANALOG DEVICES | ADP3303ARZ-3.3 | 2305721 | 1 | 2.53
VCO | - | MINI-14S | Voltage-Controlled Oscillator Surface Mount Module | Z-Communications | V950ME21-LF | - | 1 | -

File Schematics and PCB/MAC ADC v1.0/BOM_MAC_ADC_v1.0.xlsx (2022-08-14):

Bill of Materials
Assembly Name: | MAC ADC
Revision: | 1.0
Date: | 2016-09-19
Part Name | Value | Package | Description | Manufacturer | MPN | Ref. Farnell | Quantity | Approx. Unit Price | Stock
C1, C5, C6, C8 | 10 u | 0603 | Condensateur céramique multicouche CMS, 25 V, ± 20%, X5R | MURATA | ZRB18AR61E106ME01L | 2469398 | 4 | 0.254 | ok
C2, C3, C4 | 0,1 u | 0603 | Condensateur céramique multicouche CMS, 0.1 µF, 50 V, ± 10%, X7R | WALSIN | 0603B104K500CT | 2496834 | 3 | 0.0125 | ok
C7, C9 | 1 u | 0603 | Condensateur céramique multicouche CMS, 1 µF, 6.3 V, ± 10%, X5R | MURATA | GRM188R60J105KA01D | 9527699 | 2 | 0.0251 | ok
R1, R6 | 0 | - | Jumper, not mounted | - | - | - | 2 | - | -
E2, R3, R4, R5 | 49.9 | 0603 | Résistance à puce CMS, Couche épaisse, 49.9 ohm, 50 V, 63 mW, ± 1% | MULTICOMP | MC0063W0603149R9 | 1170658 | 4 | 0.0012 | ok
ADC_CON | - | - | Connector, solder | - | - | - | 1 | - | -
IN1 | - | U.FL | Connecteur coaxial / RF, Coaxial RF, Jack droit, Montage en surface vertical, 50 ohm, Laiton | MOLEX | 73412-0110 | 1340200 | 3 | 0.784 | ok
U$1 | - | MSOP-10 | Convertisseur analogique vers numérique, 16 bit, 860 Ech/s, Simple, 2 V, 5 V | TEXAS INSTRUMENTS | ADS1118IDGSR | 1947871 | 1 | 6.02 | ok
U$2 | - | SOIC-8 | Régulateur LDO Tension fixe, 4.5V à 16V, 600mV Dropout, 5Vout, 800mAout | ANALOG DEVICES | ADM7150ARDZ-5.0 | 2377358 | 1 | 7.37 | ok
U1 | - | MSOP-8 | Référence de tension, Ultra faible bruit, Série - Fixe, Série ADR441, 2.5V | ANALOG DEVICES | ADR441ARMZ | 1274160 | 1 | 5.7 | ok

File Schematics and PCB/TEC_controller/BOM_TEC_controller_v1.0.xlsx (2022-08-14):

Bill of Materials
Assembly Name: | TEC Controller
Revision: | 1.0
Date: | 2016-04-20
Part Name | Value | Package | Description | Manufacturer | MPN | Ref. Farnell | Quantity | Approx. Unit Price
C1, C2, C7 | 22u | 1210 | Condensateur céramique multicouche CMS, Série M, 22 µF, ± 20%, X5R, 6.3 V | TAIYO YUDEN | JMK325BJ226MM-T | 2112744 | 3 | 1.17
C3, C5, C6 | 0.1u | 0805 | Condensateur céramique multicouche CMS, 0.1 µF, ± 10%, X7R, 50 V | WALSIN | 0805B104K500CT | 2496944 | 3 | 0.0148
C4 | 0.33u | 0805 | Condensateur céramique multicouche, C Series, Série C, 0.33 µF, ± 10%, X7R, 50 V | TDK | C2012X7R1H334K125AA | 2346946 | 1 | 0.157
C8 | 10 u | 1206 | Condensateur céramique multicouche CMS, Série M, 10 µF, ± 10%, X7R, 6.3 V | TAIYO YUDEN | JMK316B7106KL-T | 2112908 | 1 | 0.218
C9, C11, C17, C18 | 1u | 0603 | Condensateur céramique multicouche CMS, Série GRM, 1 µF, ± 10%, X5R, 6.3 V | MURATA | GRM188R60J105KA01D | 9527699 | 4 | 0.0314
C10 | 330p | 0603 | Condensateur céramique multicouche CMS, Série MC, 330 pF, ± 5%, C0G / NP0, 50 V | MULTICOMP | MC0603N331J500CT | 1759076 | 1 | 0.0139
C12, C13, C19, C20 | 0.1u | 0603 | Condensateur céramique multicouche CMS, 0.1 µF, ± 10%, X7R, 50 V | WALSIN | 0603B104K500CT | 2496834 | 4 | 0.0126
C14, C15 | 0.1u SM | 1210 | Condensateur film, Série ECHU(X), 0.1 µF, ± 5%, Polyphénylène sulfide (PPS) | PANASONIC | ECHU1C104JX5 | 9695117 | 2 | 0.574
C16 | 4.7u | 1206 | Condensateur tantale CMS, Série TAJ, 4.7 µF, ± 20%, 10 V | AVX | TAJA475M010RNJ | 2333018 | 1 | 0.638
I/O |  | 53398-08 | Connecteur fil-à-carte, Série PicoBlade 53398, Montage CMS, Embase, 8, 1.25 mm | MOLEX | 53398-0871 | 1125371 | 1 | 1.43
L1, L2 | 10 uH | INDM7676X435N | Inductance de puissance CMS, Série DR74, 10 µH, ± 20%, Blindé, 2.41 A | COILTRONICS | DR74-100-R | 1463480 | 2 | 2.42
R1, R2, R3, R10, R11 | 10k | 0603 | Résistance CMS, Céramique, Série MCMR, 10 kohm, 100 mW, ± 1%, 75 V | MULTICOMP | MCMR06X1002FTL | 2073349 | 5 | 0.0149
R4 | 82k | 0603 | Résistance CMS, Couche épaisse, Série AEC-Q200 ERJ, 82 kohm, 100 mW, ± 1%, 75 V | PANASONIC | ERJ3EKF8202V | 2303225 | 1 | 0.0083
R5 | 9.09k | 0603 | Résistance CMS, Couche mince, Série CPF, 9.09 kohm, 63 mW, ± 1%, 60 V | TE CONNECTIVITY | CPF0603F9K09C1 | 1527577 | 1 | 0.099
R6 | 1k | 0603 | Résistance CMS, Céramique, Série MCMR, 1 kohm, 100 mW, ± 1%, 75 V | MULTICOMP | MCMR06X1001FTL | 2073348 | 1 | 0.0149
R7 | 100k | 0603 | Résistance CMS, Couche épaisse, Série RC, 100 kohm, 100 mW, ± 1%, 50 V | YAGEO | RC0603FR-13100KL | 2309107 | 1 | 0.008
R8 | 10M | 0603 | Résistance CMS, Couche épaisse, Série AEC-Q200 CRCW, 10 Mohm, 100 mW, ± 1% | VISHAY | CRCW060310M0FKEA | 1469750 | 1 | 0.021
R9 | 50k | 0603 | Missing
RS | 0.5 | 1206 | Résistance CMS, Série AEC-Q200 LR, 0.5 ohm, 500 mW, ± 1%, 200 V | WELWYN | LR1206-R50FW | 1100339 | 1 | 0.458
TEC |  | F09HP | Connecteur Sub D standard, Angle Droit, Série 182, DE, Embase, 9, Corps en acier | NORCOMP | 182-009-213R171 | 2294287 | 1 | 1.79
U$1 |  | SSOP-28 | High Efficiency Thermoelectric Cooler Controller | Linear Technology | LTC1923EGN#PBF | (RS) 786-9884 | 1 | 28.19
U$2, U$3 |  | SOIC-8 | MOSFET double, Canal N et P, 6 A, 30 V, 38 mohm, 10 V, 1 V | VISHAY | SI4532CDY-T1-GE3 | 1779268 | 2 | 0.667
U$6 |  | SOT-223 | Linear Voltage Regulator, Fixed, 7V To 25V In, 5V And 0.5A Out | TEXAS INSTRUMENTS | UA78M05QDCYRG4Q1 | 2383041 | 1 | 0.718
U1 |  | MSOP-8 | Amplificateur d'instrumentation, 1 amplificateur, 20 µV, 0.2 V/µs, 200 kHz, 2.7V à ± 5.5V | Linear Technology | LTC2053IMS8#PBF | 1663681 | 1 | 6.9524
U2 |  | SOIC-8 | Convertisseur numérique vers analogique, 14 bit, Série, 2.7V à 5.5V | Linear Technology | LTC1658CS8#PBF | 1663655 | 1 | 10.09
 |  |  |  |  |  |  |  | 55.7112

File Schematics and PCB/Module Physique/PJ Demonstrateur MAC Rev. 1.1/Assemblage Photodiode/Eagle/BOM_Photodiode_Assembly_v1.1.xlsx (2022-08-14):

Bill of Materials
Assembly Name: | Photodiode Assembly
Revision: | 1.1
Date: | 2016-04-21
Author: | J. Rutkowski
Part Name | Value | Package | Description | Manufacturer | MPN | Disrtibutor | Distributor PN | Quantity | Approx. Unit Price
C1 | 6p | 0805 | Condensateur céramique multicouche CMS, Série MC, 6 pF, ± 0.5pF, C0G / NP0, 50 V | MULTICOMP | MC0805N6R0D500CT | Farnell | 1759185 | 1 | 0.0578
C2 | 0,1u | 0805 | Condensateur céramique multicouche CMS, 0.1 µF, ± 10%, X7R, 50 V | WALSIN | 0805B104K500CT | Farnell | 2496944 | 1 | 0.0172
C3 | 1u | 0805 | Condensateur céramique multicouche CMS, Série C, 1 µF, ± 10%, X7R, 25 V | KEMET | C0805C105K3RACTU | Farnell | 1637035 | 1 | 0.0636
R1 | 220k | 0805 | Résistance CMS, Couche mince, Série RR, 220 kohm, 100 mW, ± 0.1%, 100 V | SUSUMU | RR1220P-224-B-T5 | Farnell | 1653300 | 1 | 0.534
R2 | 1k | 0805 | Résistance CMS, Couche métallique, Série AEC-Q200 ERA, 1 kohm, 125 mW, ± 0.1%, 200 V | PANASONIC | ERA6ARB102V | Farnell | 1717624 | 1 | 1.21
D1 |  | SMD | PHOTODIODE 900NM 5 2MM | VISHAY | TEMD5020X01 | Farnell | 2251275 | 1 | 1.25
IC1 |  | SOIC-8 | Amplificateur opérationnel, Simple, 1.9 MHz, 1 amplificateur, 3 V/µs, 5V à 36V | ANALOG DEVICES | AD820ARZ | Farnell | 9426469 | 1 | 4.01
 |  |  |  |  |  |  |  |  | 7.1426 | unitaire

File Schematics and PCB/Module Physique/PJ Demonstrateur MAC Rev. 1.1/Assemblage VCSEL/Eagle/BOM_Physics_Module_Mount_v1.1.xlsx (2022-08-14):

Bill of Materials
Assembly Name: | Physics Module Mount
Revision: | 1.1
Date: | 2016-04-21
Author: | J. Rutkowski
Part Name | Value | Package | Description | Manufacturer | MPN | Disrtibutor | Distributor PN | Quantity | Approx. Unit Price
C1 | 0.01u | 0603 | Condensateur céramique multicouche CMS, 0.01 µF, ± 5%, X7R, 50 V | WALSIN | 0603B103J500CT | Farnell | 2496824 | 1 | 0.0117
LASER_RF |  | SMA | Connecteur coaxial / RF, Coaxial SMA, Jack droit, A souder, 50 ohm, Cuivre-béryllium | JOHNSON | 142-0701-851 | Farnell | 1019325 | 1 | 4.97
PHOTODIODE_SIG |  | U.FL | Connecteur coaxial / RF, Coaxial RF, Jack droit, Montage en surface vertical, 50 ohm, Laiton | MOLEX | 73412-0110 | Farnell | 1340200 | 1 | 0.784
Q1 |  | TO-46 | 895±0.5 nm single mode VCSEL on a TO can six leaded can with TEC & Thermistor | VIXAR | 895S-0-BC02 | Laser 2000 | VIX-895S-0000-BC04 | 1 | 400
SV1, SV2 |  |  | Connecteur carte-à-carte, Bas Profil, Série BBL, Traversant, Embase, 10, 2.54 mm | SAMTEC | BBL-110-G-E | Farnell | 1667438 | 2 | 4.05
U1 |  | PL-146 | Surface Mount Bias-Tee, 50 Ohm, Wideband 10 MHz to 10 GHz | Mini-Circuits | TCBT-14R+ | Elexience | TCBT-14R+ | 1 | 10

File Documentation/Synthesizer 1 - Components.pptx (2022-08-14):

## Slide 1

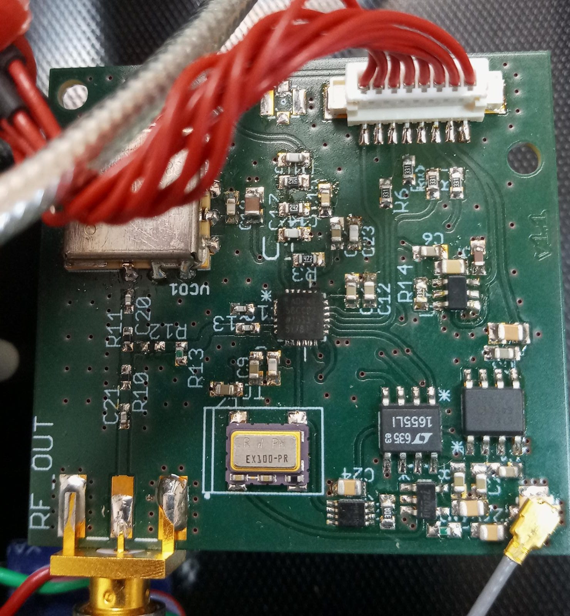
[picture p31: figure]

C16: 22nF

C16: 2x330pF

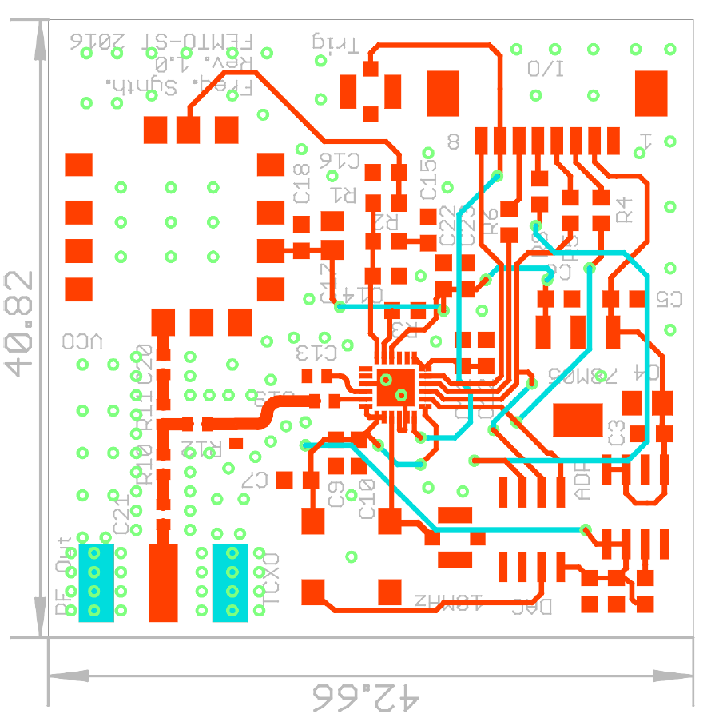
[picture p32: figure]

R1: 5.1kΩ

R1: 5.1kΩ

C15: 680nF

C15: 8.2nF

R2: 2.4kΩ

R2: 2.4kΩ

C14: 47nF

C14: 330pF

R3: 4.7kΩ

R3: 4.7kΩ

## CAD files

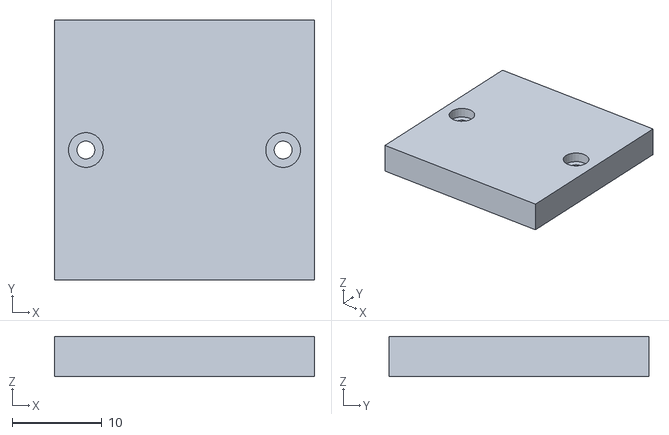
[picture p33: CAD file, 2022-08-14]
Schematics and PCB/Module Physique/PJ Demonstrateur MAC Rev. 1.1/Capot/Capot_MAC_v1.1.stl
29.0 x 29.0 x 4.50

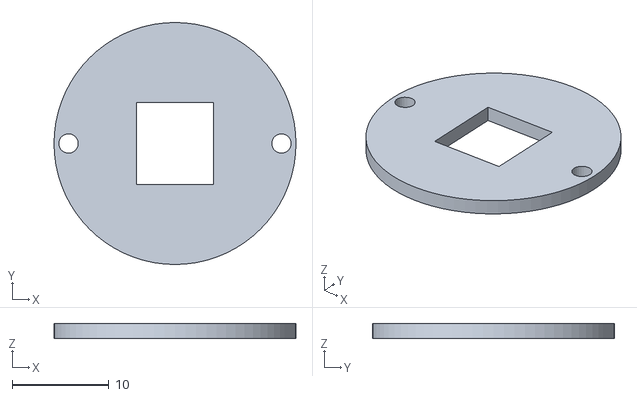
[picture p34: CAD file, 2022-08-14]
Schematics and PCB/Module Physique/PJ Demonstrateur MAC Rev. 1.1/Entretoise/Spacer_MAC_v1.1.stl
25.0 x 25.0 x 1.50

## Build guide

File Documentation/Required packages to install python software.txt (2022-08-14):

Packages installed to run the software:

python -m pip install pyserial
pip install pyqtgraph
pip install PyQt6
pip install pyyaml

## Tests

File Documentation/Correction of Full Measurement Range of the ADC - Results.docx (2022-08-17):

# Correction of Full Measurement Range of the ADC ADS1118

Clock 1 - Before:

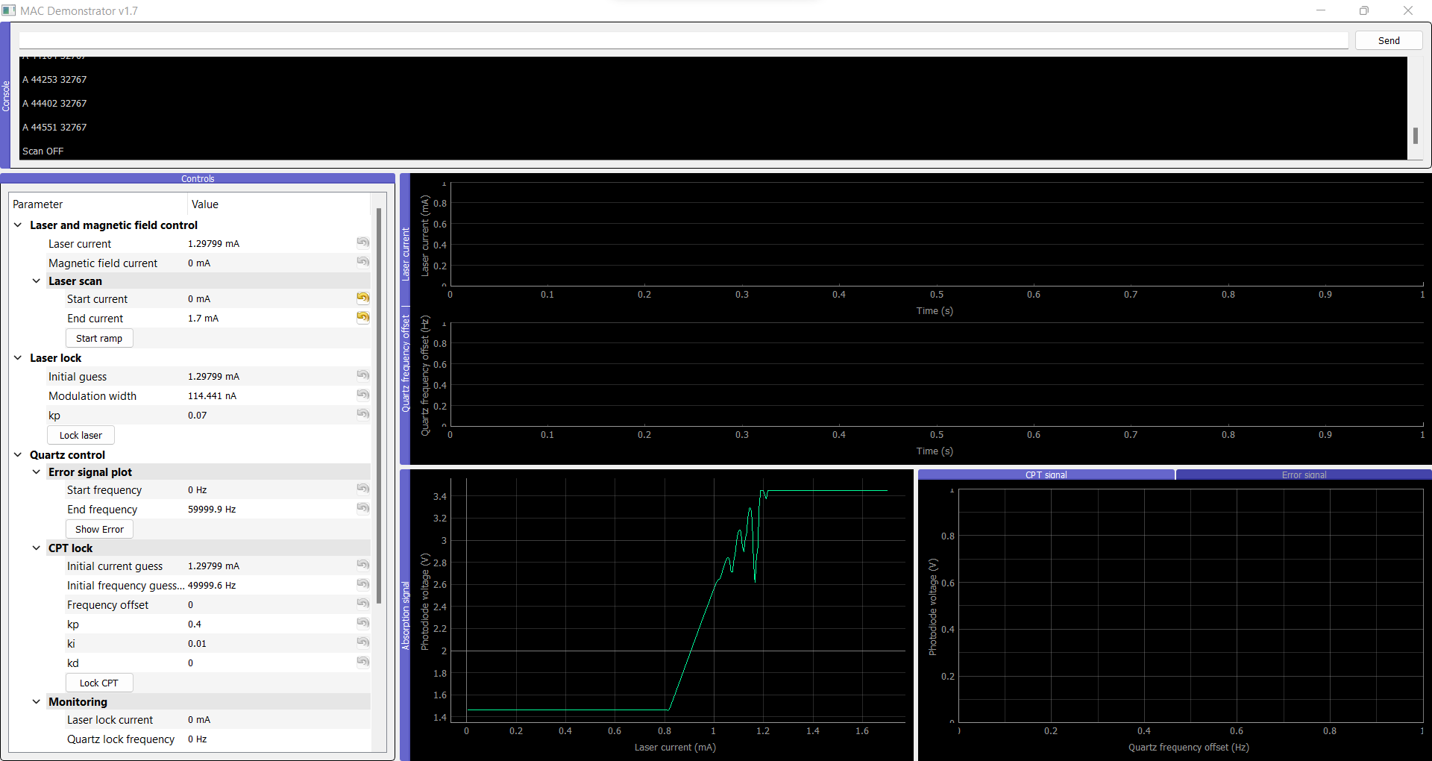
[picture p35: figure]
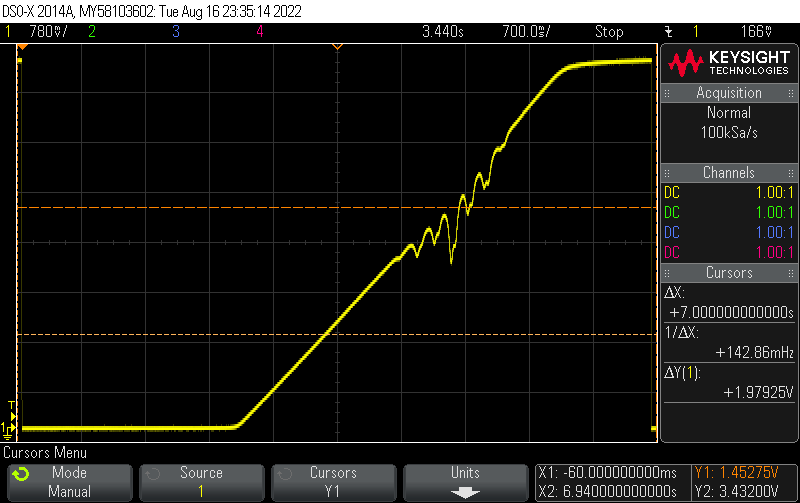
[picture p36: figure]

Clock 1 - After (Arduino and Python code modified):

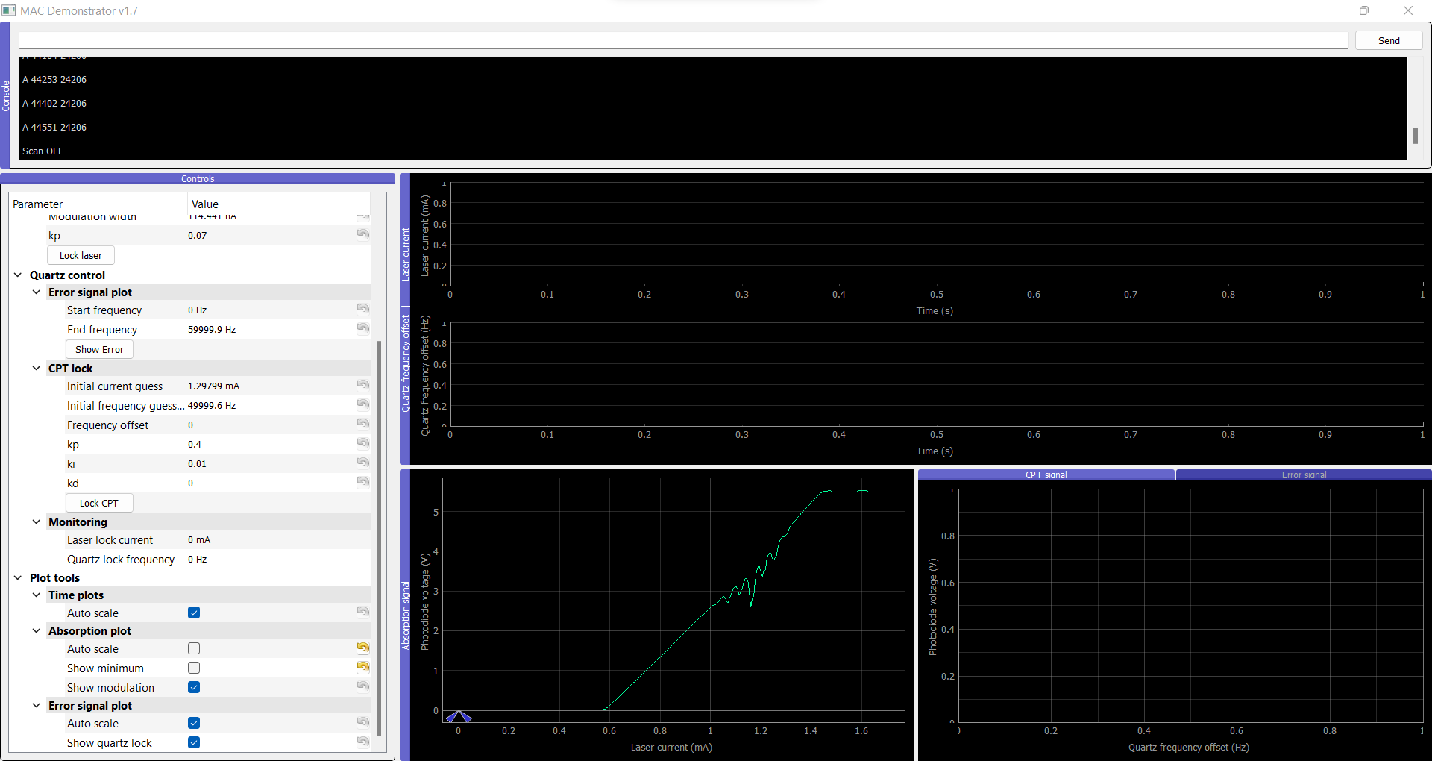
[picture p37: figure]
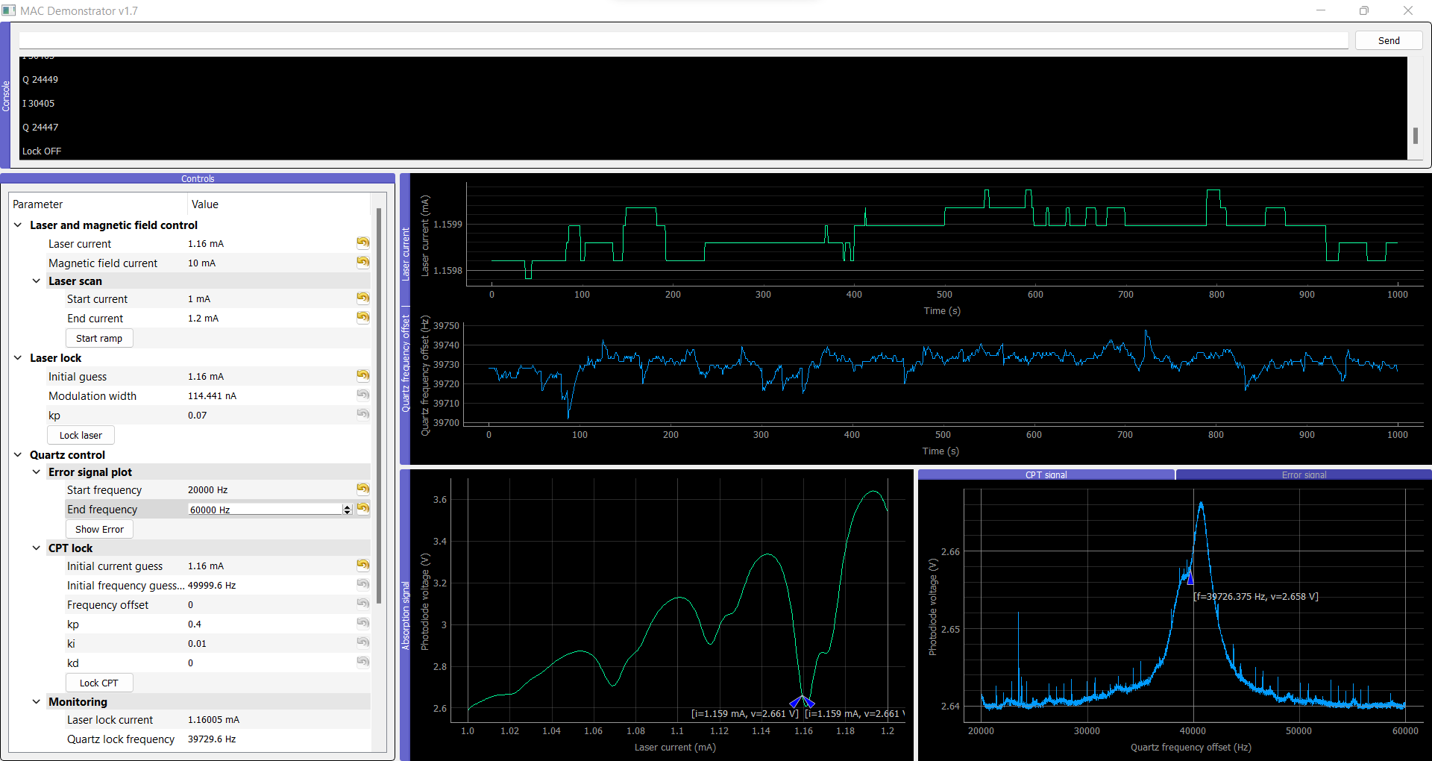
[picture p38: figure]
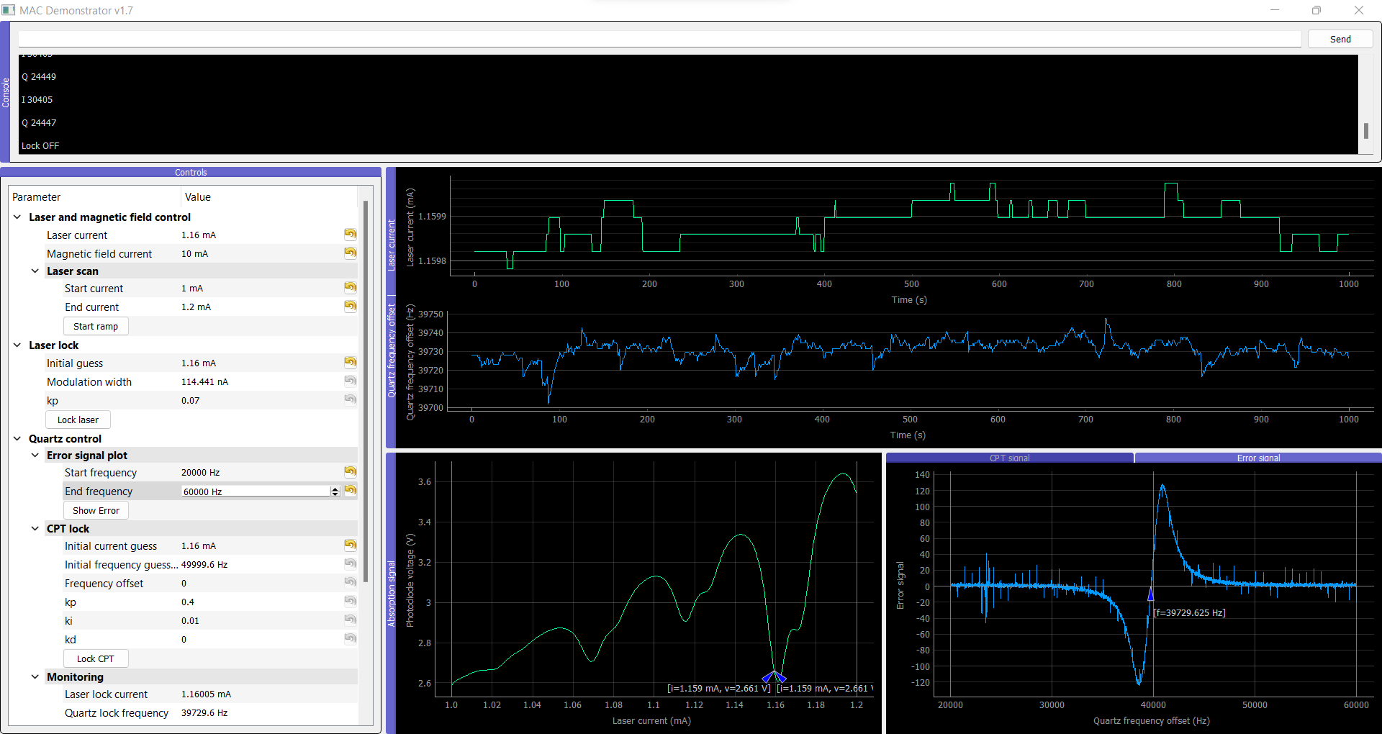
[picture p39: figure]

Clock 3 - After:

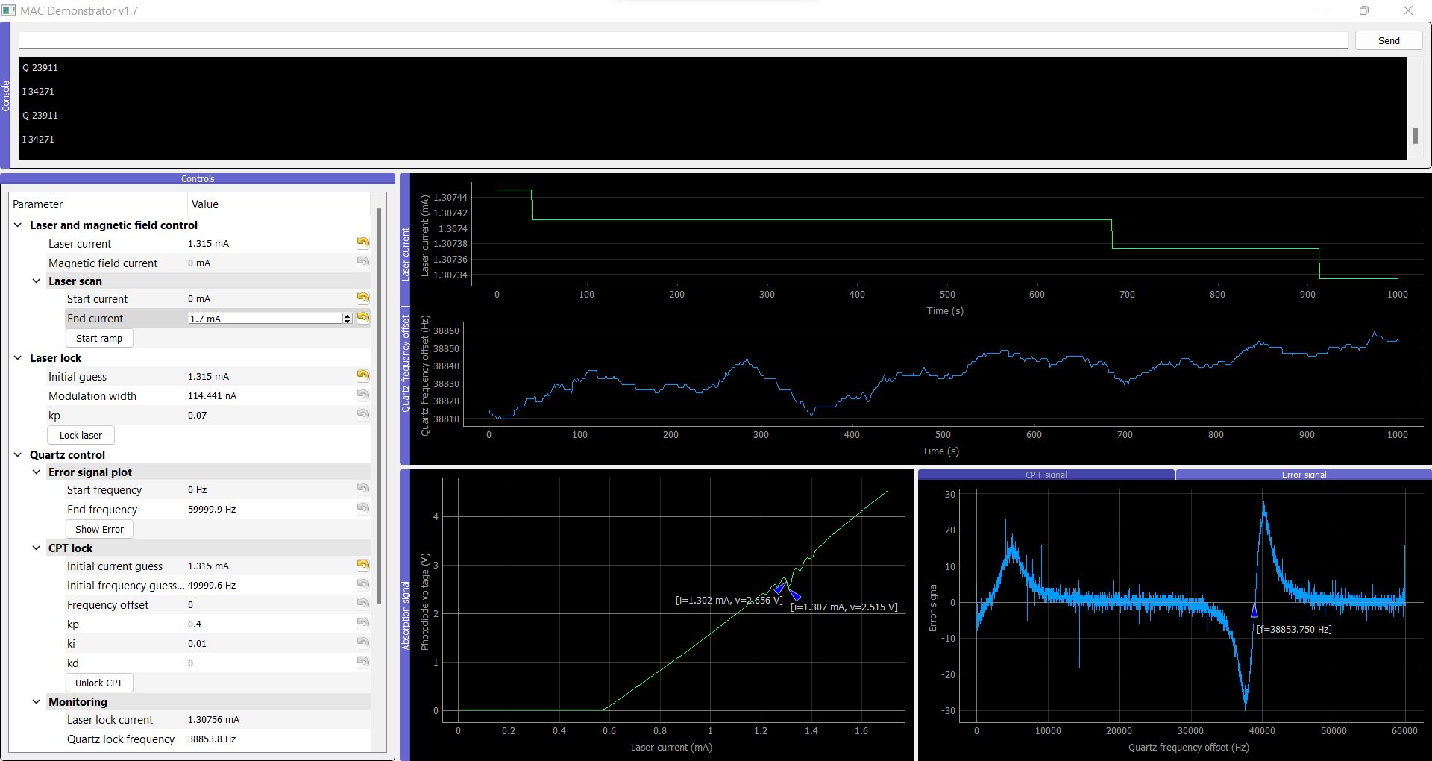
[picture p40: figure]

Clock 2 - After:

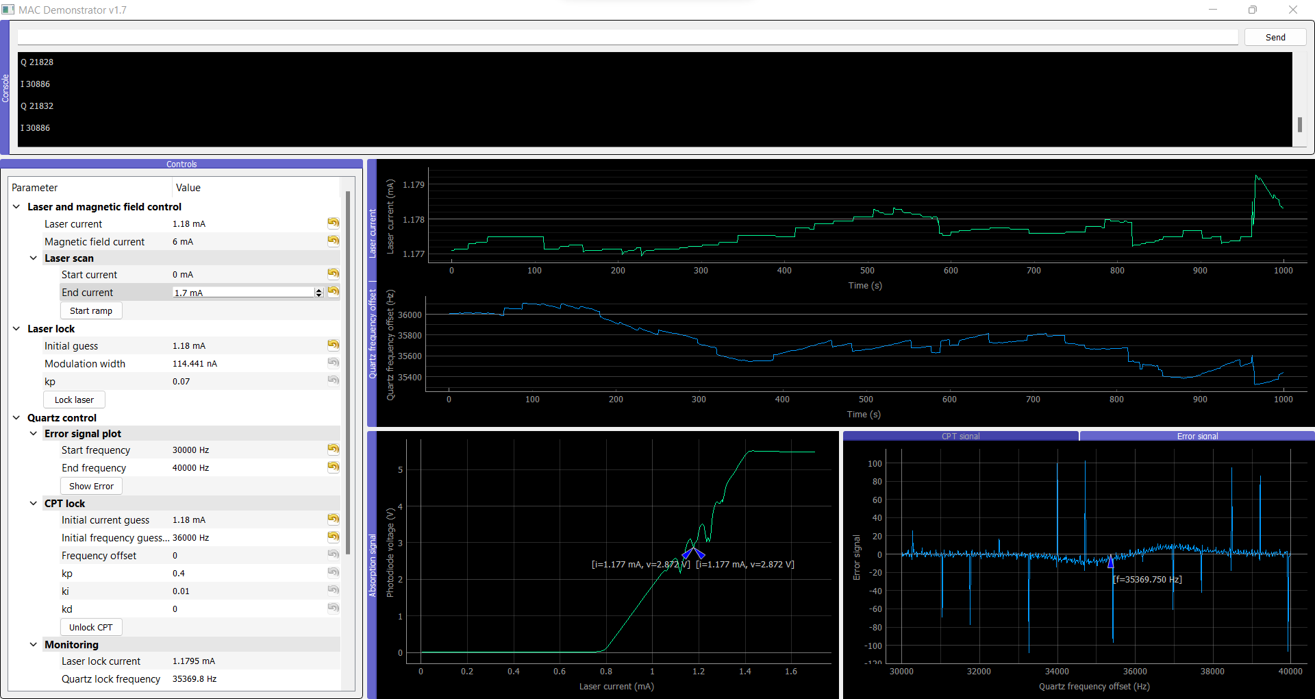
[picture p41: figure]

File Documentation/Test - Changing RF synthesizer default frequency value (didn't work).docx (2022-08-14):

RF synthesizer default value: 4596301446 Hz

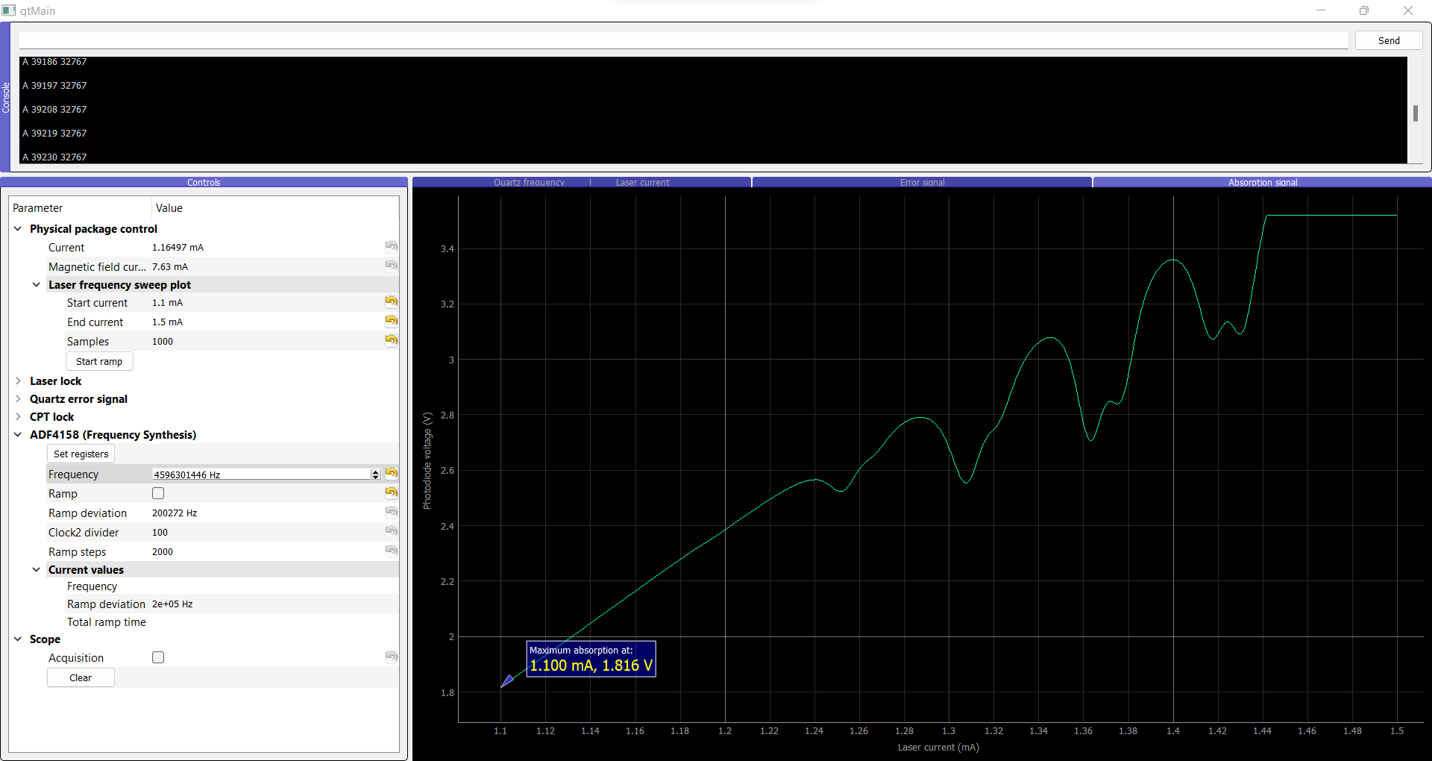
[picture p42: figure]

Absorption at: 2.708 V

Modification: 4566301446 Hz

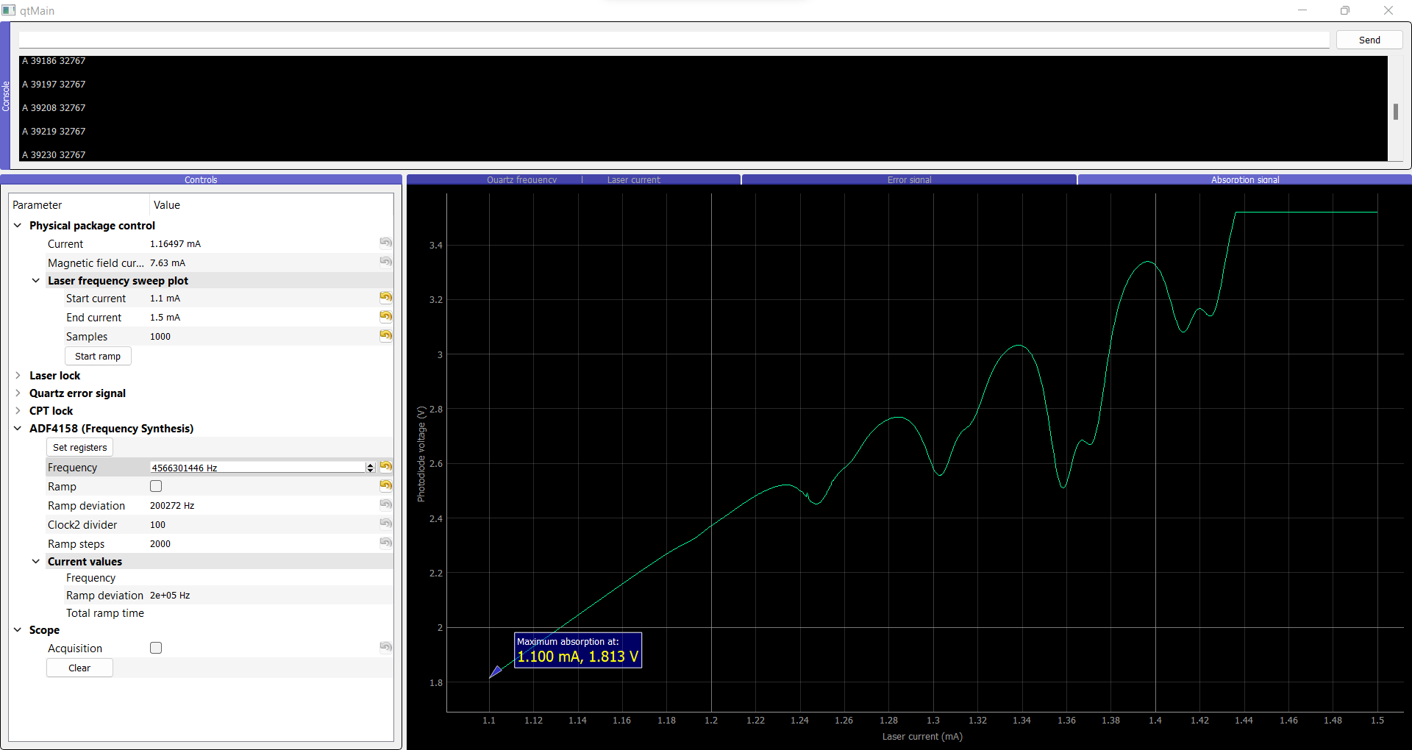
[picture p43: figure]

Absorption at: 2.51 V

Modification: 4556301446 Hz

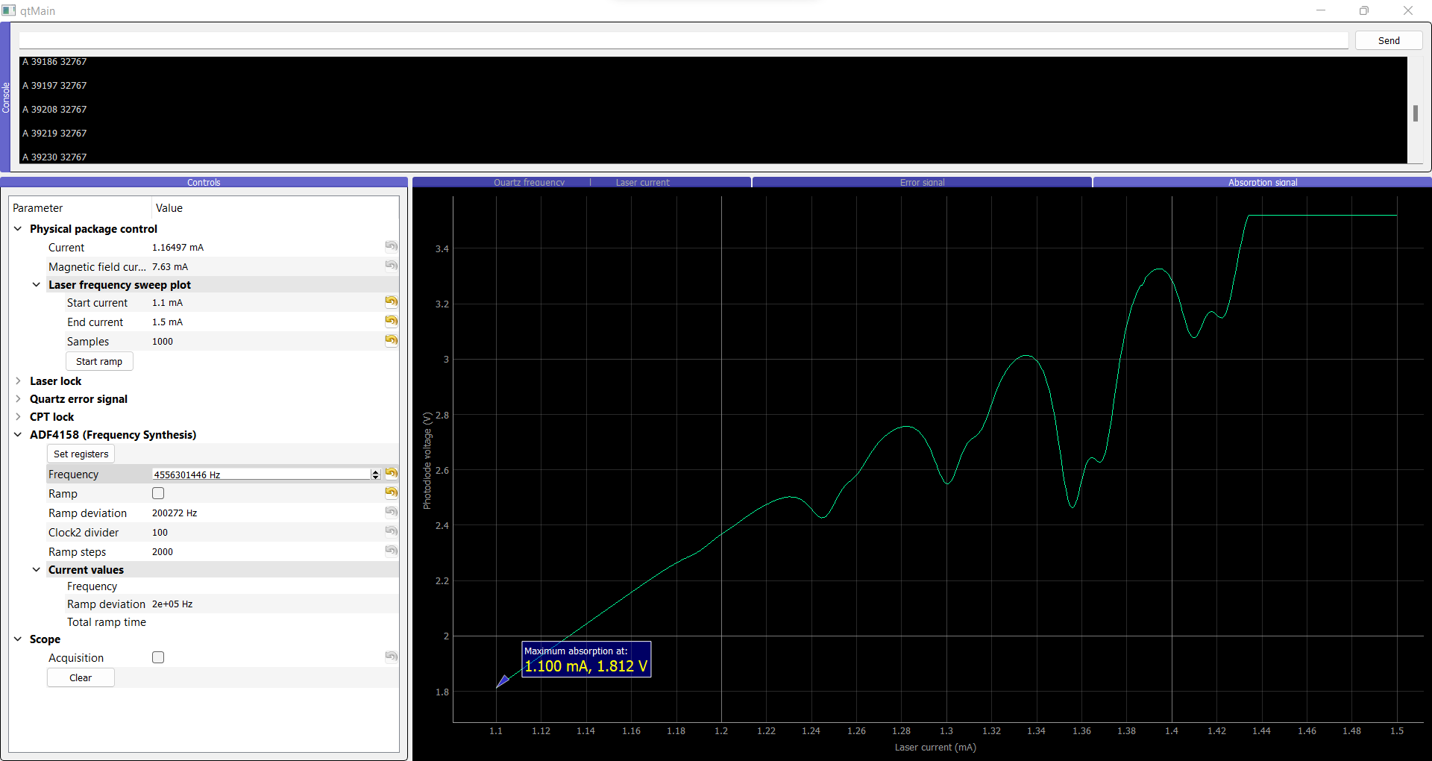
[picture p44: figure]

Absorption at: 2.46 V

At 4596376300 “0” is at 23000

Conclusion: Changing the PLL frequency seems to increase the absorption but it is no longer possible to find a CPT signal when doing a quartz VCO scan. This was not a good solution and was not implemented in the final code.

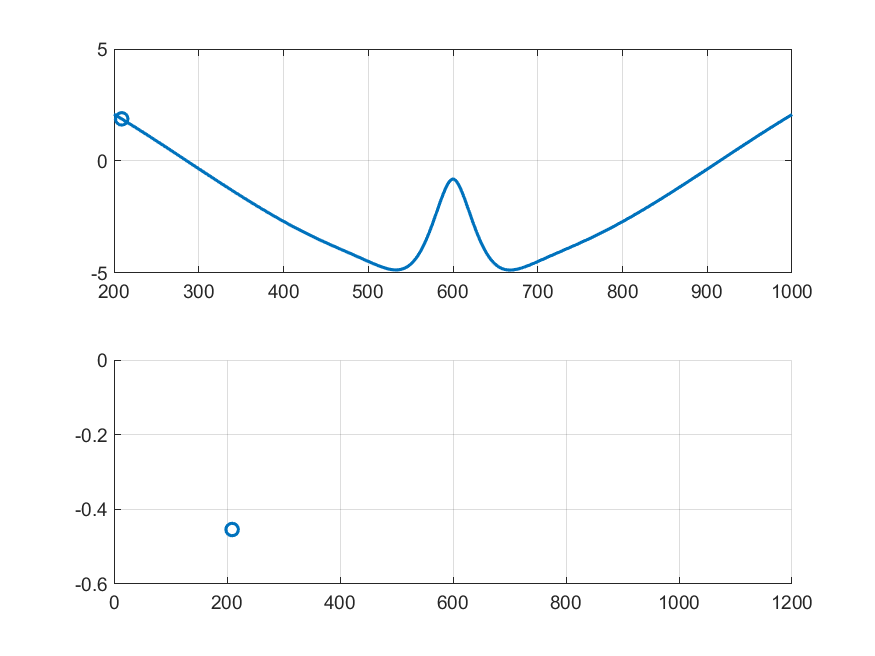
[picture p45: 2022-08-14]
Internship Project M1 (Carlos RIVERA)/Images/test.gif

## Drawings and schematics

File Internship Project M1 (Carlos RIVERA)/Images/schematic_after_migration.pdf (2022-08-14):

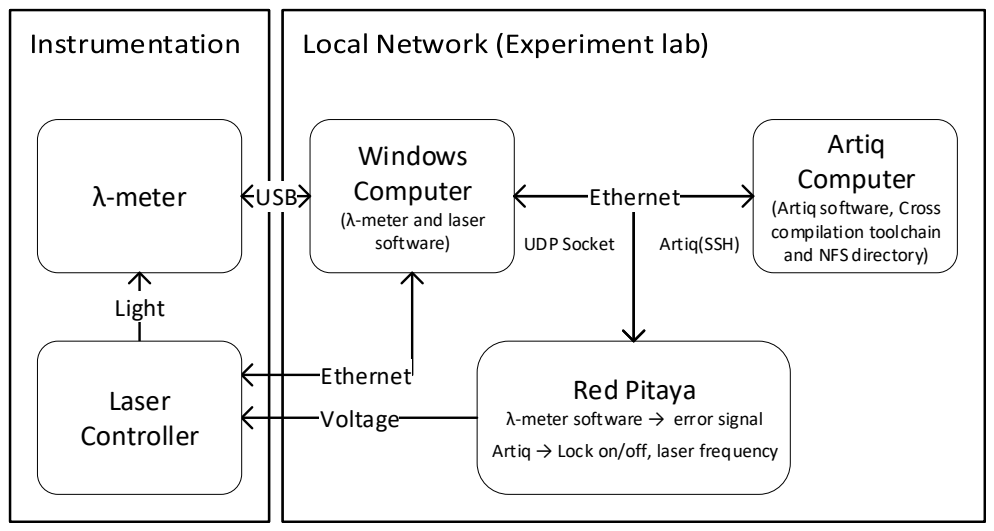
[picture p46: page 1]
λ-meter; Red Pitaya; Light; Voltage; USB; UDP Socket; Artiq(SSH); Ethernet; Laser Controller

Windows
Computer
(λ-meter and laser
software)

Artiq
(Artiq software, Cross
compilation toolchain
and NFS directory)

λ-meter software → error signal
Artiq → Lock on/off, laser frequency

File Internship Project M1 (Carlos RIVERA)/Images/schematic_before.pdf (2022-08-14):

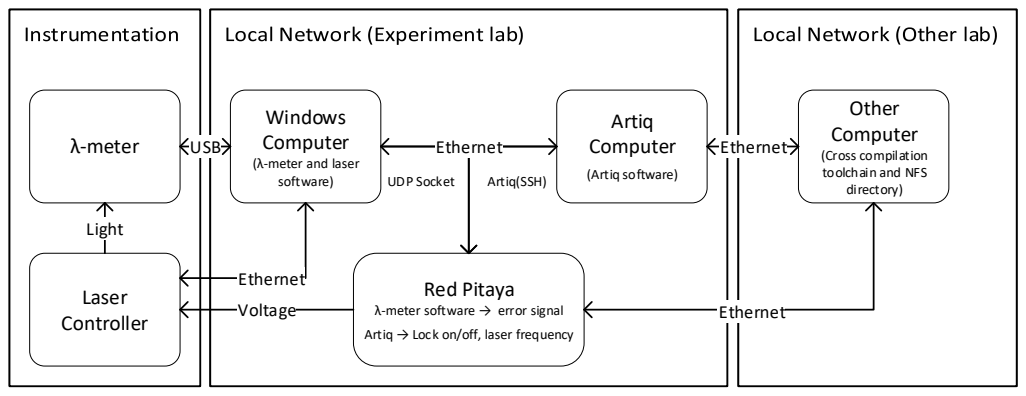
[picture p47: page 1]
λ-meter; Artiq Computer; (Artiq software); Red Pitaya; Laser Controller; Light; Voltage; USB; UDP Socket; Artiq(SSH); Ethernet

Windows
Computer
(λ-meter and laser
software)

Other
(Cross compilation
toolchain and NFS
directory)

λ-meter software → error signal
Artiq → Lock on/off, laser frequency

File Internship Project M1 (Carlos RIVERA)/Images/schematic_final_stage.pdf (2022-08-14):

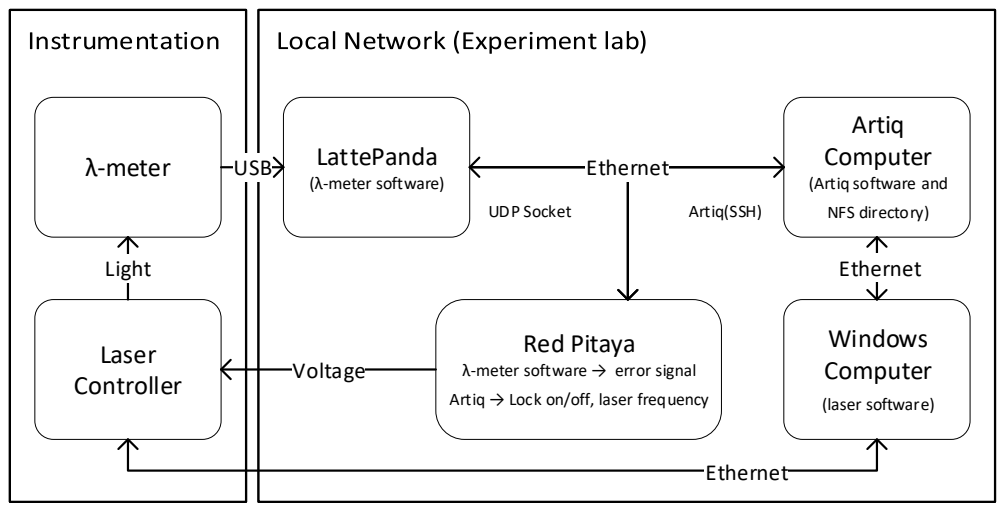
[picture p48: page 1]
λ-meter; LattePanda; (λ-meter software); Red Pitaya; Laser Controller; Light; Voltage; USB; UDP Socket; Artiq(SSH); Ethernet; Windows Computer; (laser software)

Artiq
Computer
(Artiq software and
NFS directory)

λ-meter software → error signal
Artiq → Lock on/off, laser frequency

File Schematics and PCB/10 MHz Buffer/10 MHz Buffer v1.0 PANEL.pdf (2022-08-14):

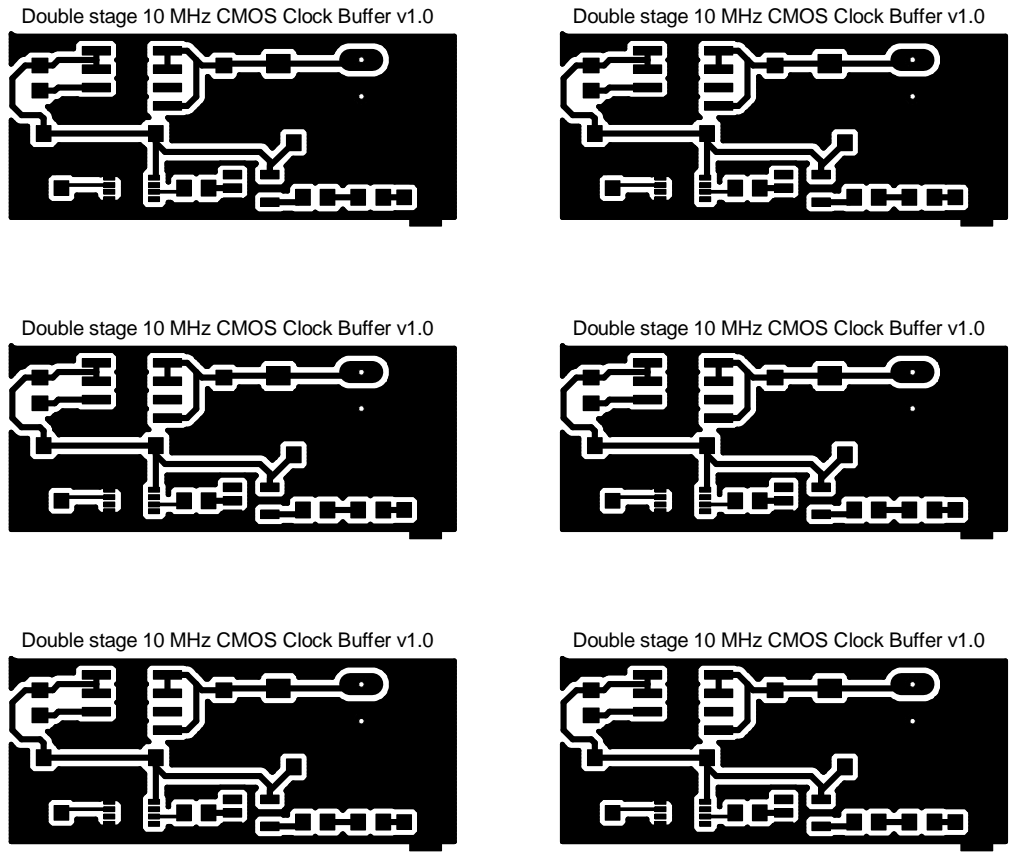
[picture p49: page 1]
Double stage 10 MHz CMOS Clock Buffer v1.0

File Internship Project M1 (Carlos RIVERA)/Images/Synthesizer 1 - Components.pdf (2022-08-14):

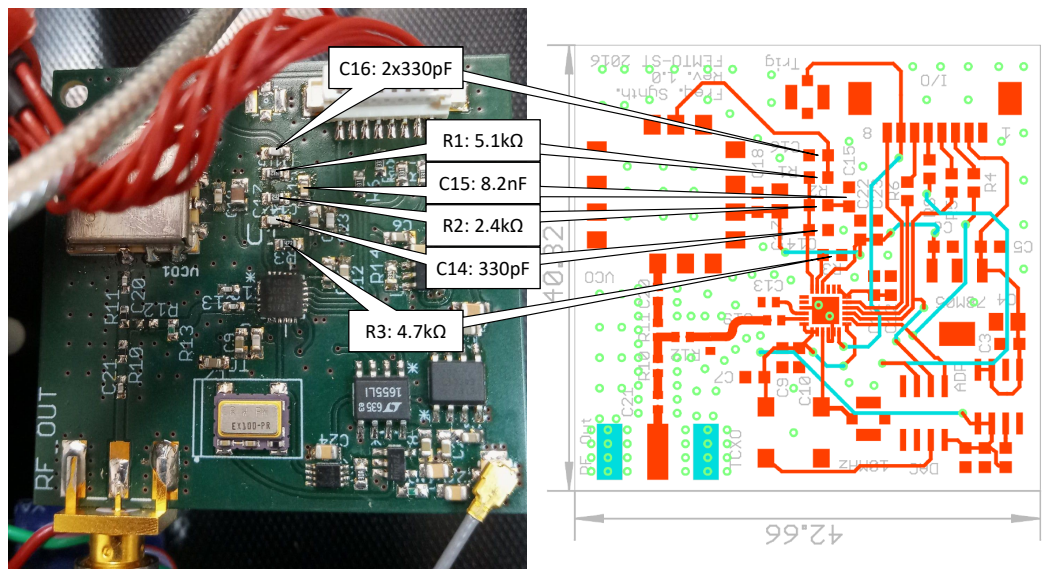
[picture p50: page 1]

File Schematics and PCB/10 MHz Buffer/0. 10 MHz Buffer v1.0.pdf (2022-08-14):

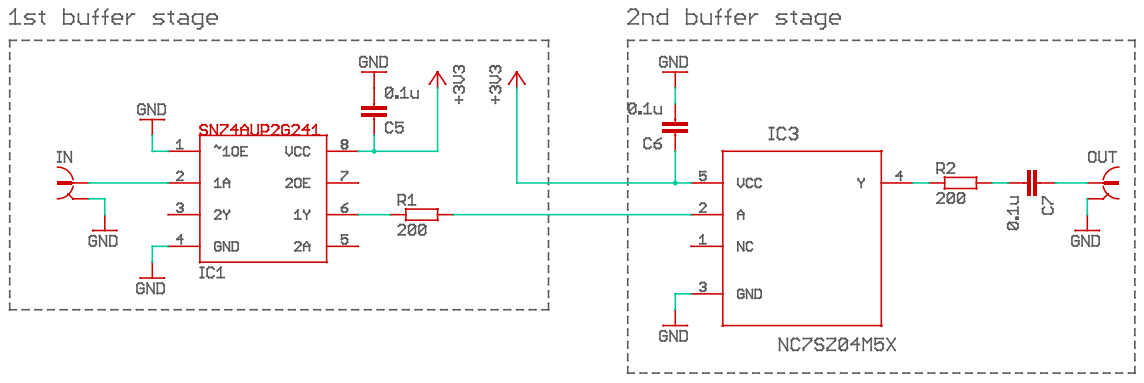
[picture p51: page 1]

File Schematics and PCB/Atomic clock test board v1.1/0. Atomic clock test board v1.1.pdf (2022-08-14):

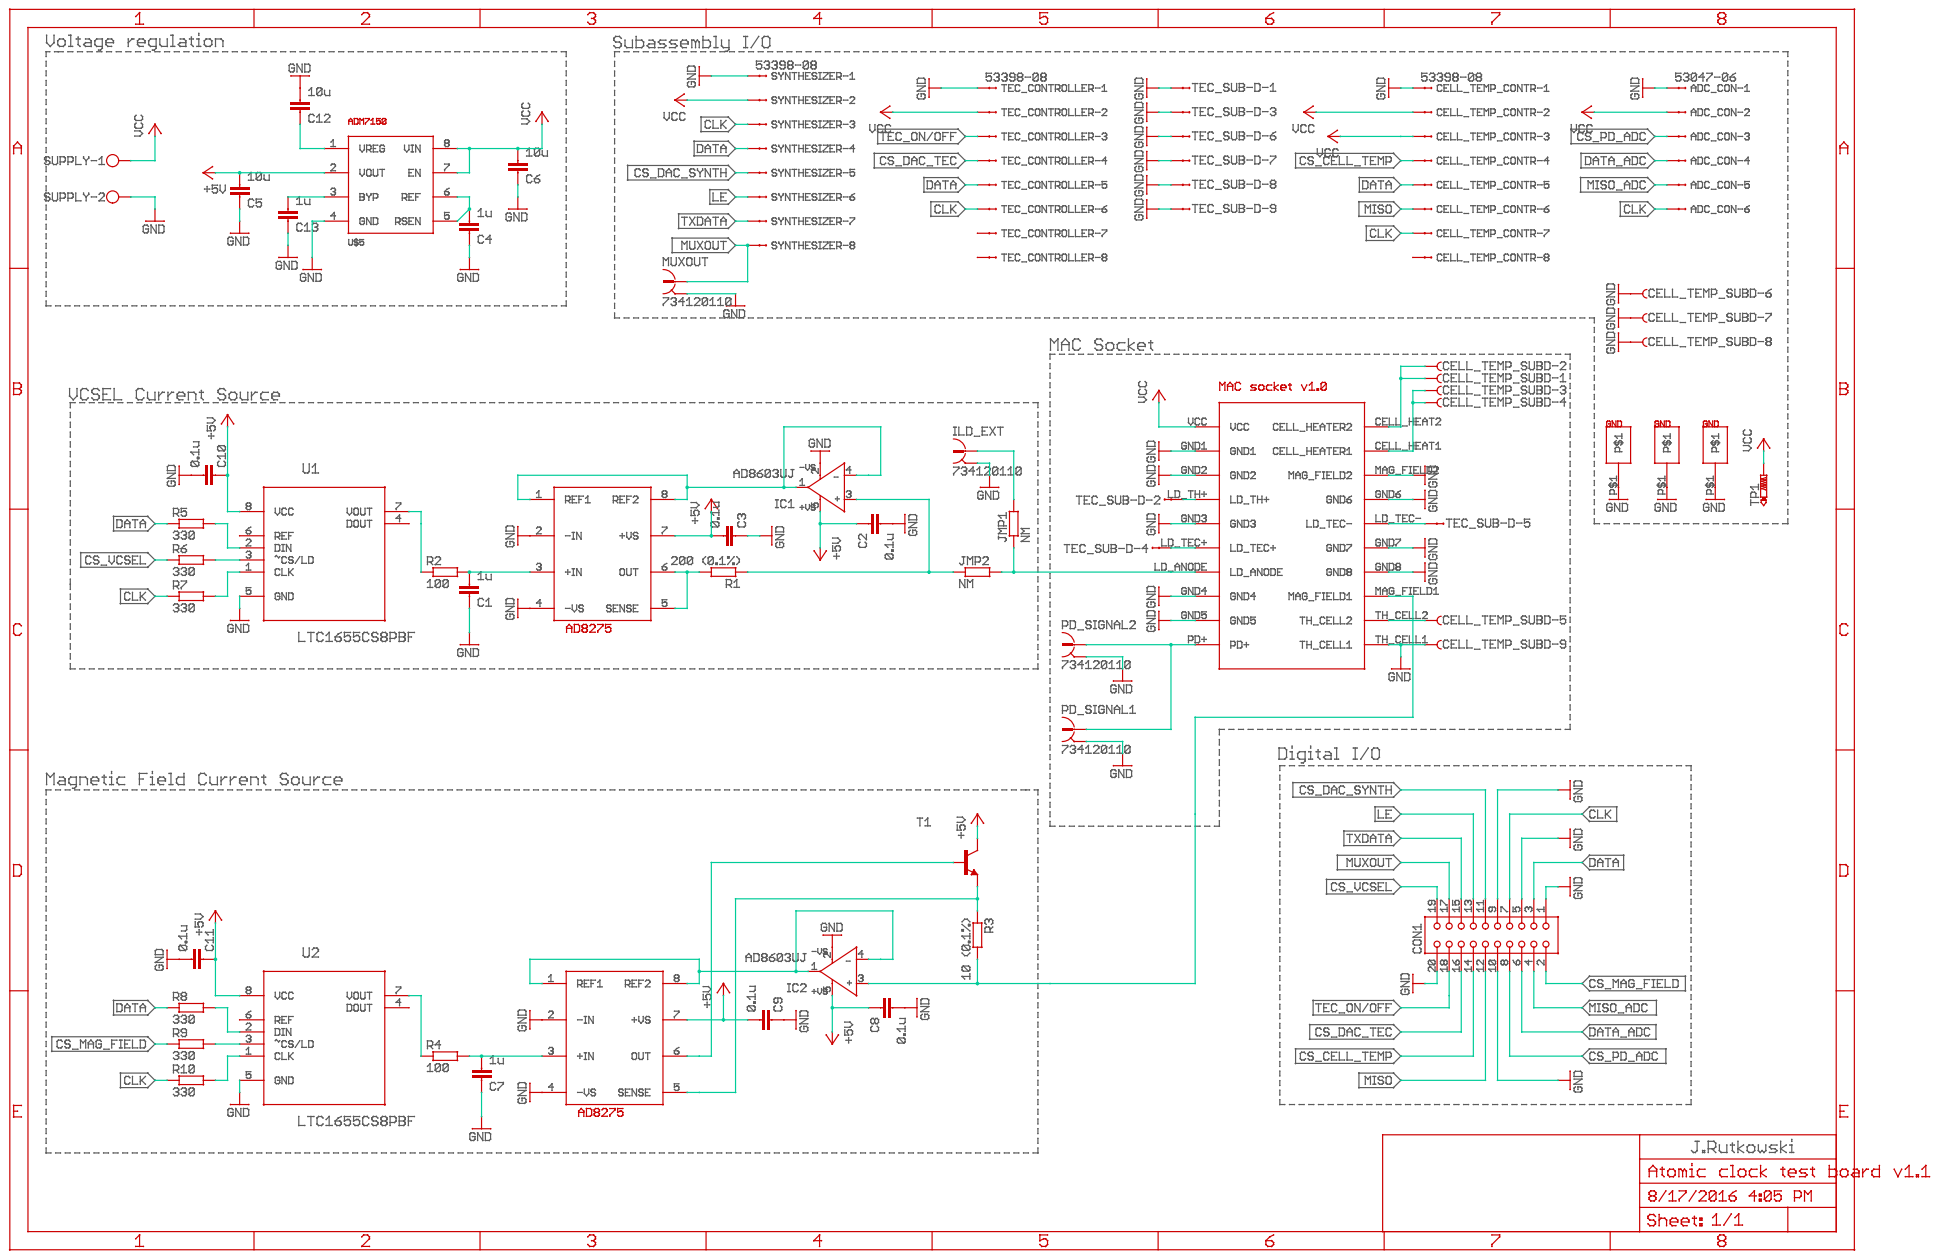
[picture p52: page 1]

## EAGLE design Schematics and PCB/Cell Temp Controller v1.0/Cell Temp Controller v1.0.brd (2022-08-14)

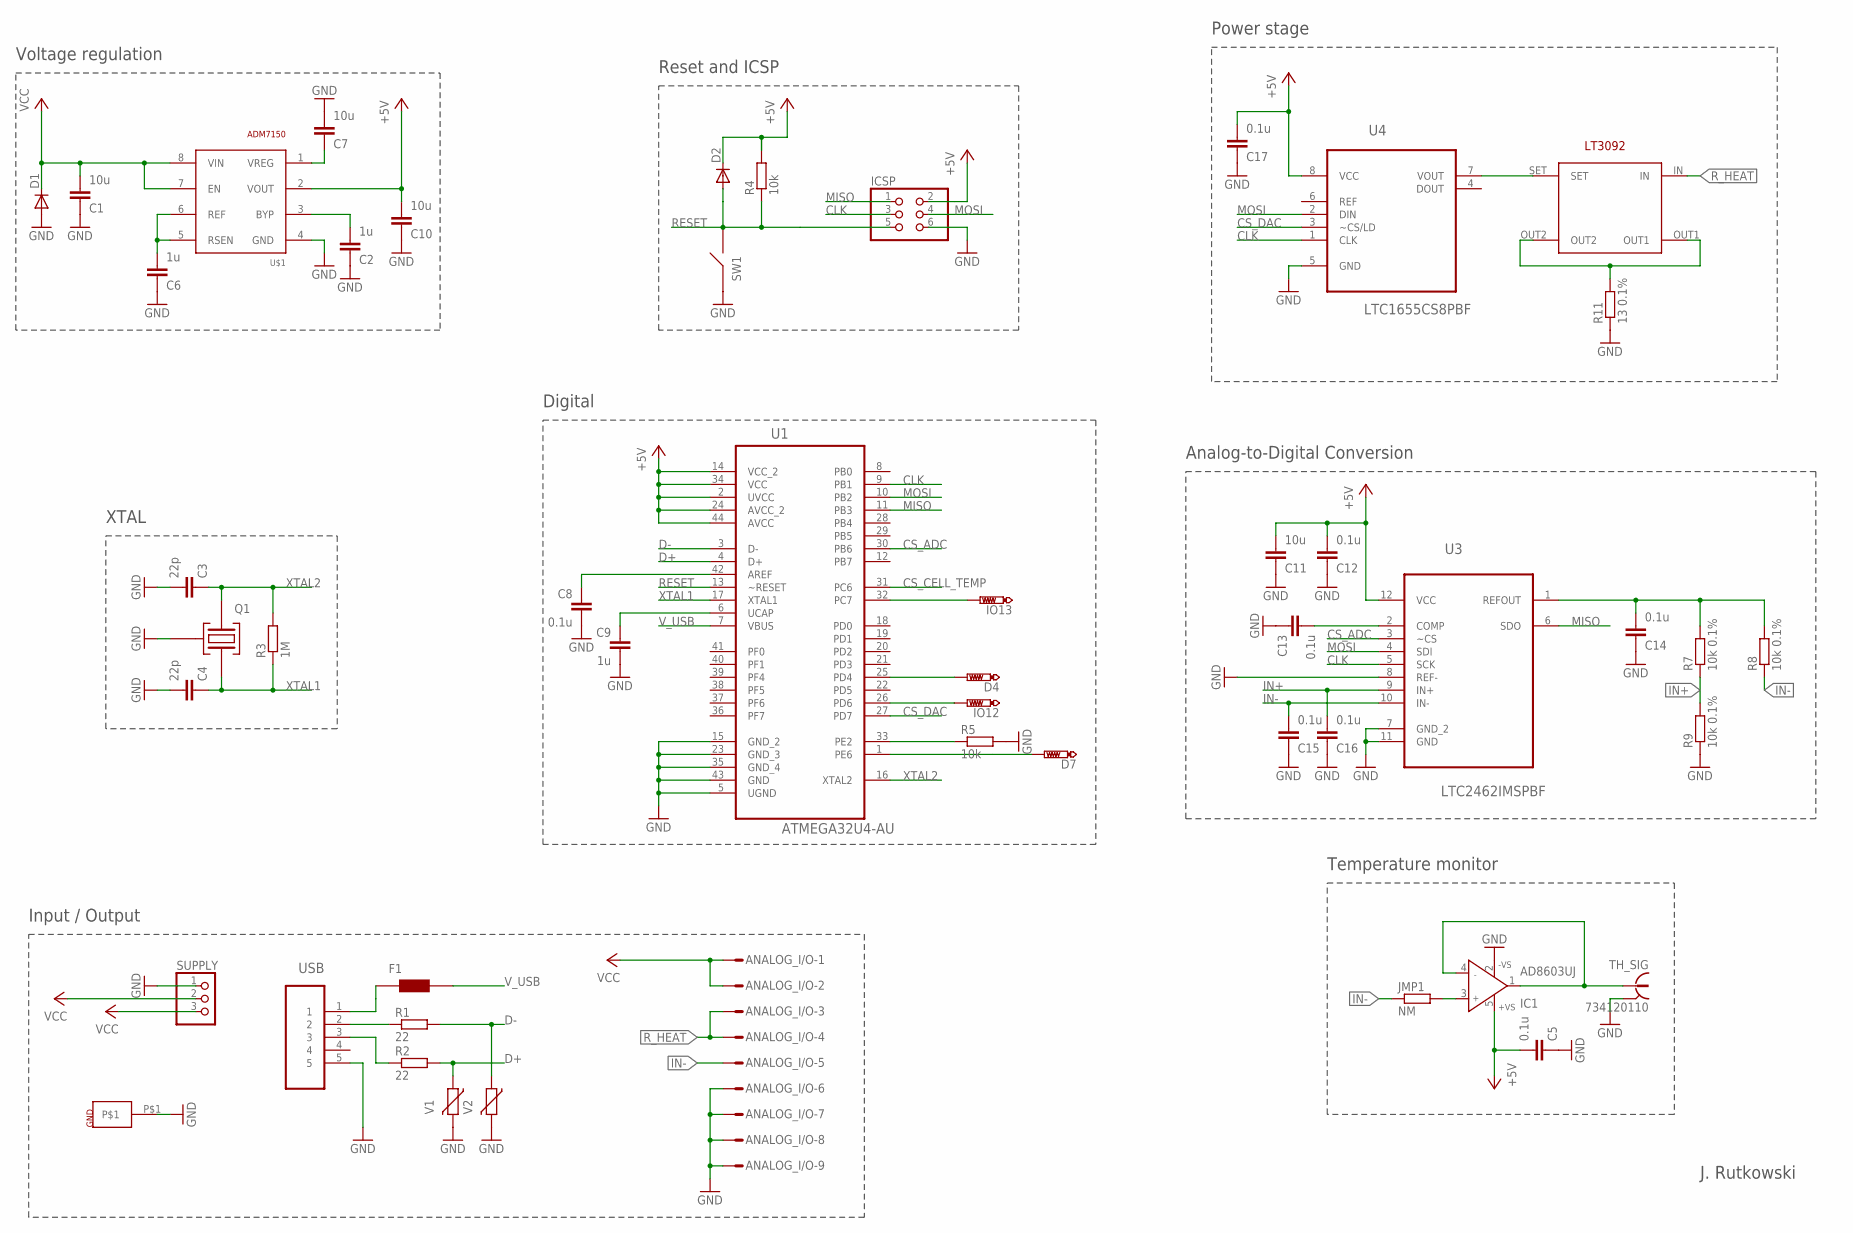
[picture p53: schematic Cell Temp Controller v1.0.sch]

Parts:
ANALOG_I/O: M09HPS; M09HP
C1, C7, C10, C11: 10u; C0603K
C2, C6, C9: 1u; C0603K
C3, C4: 22p; C0603K
C5, C8, C12, C13, C14, C15, C16, C17: 0.1u; C0603K
D1, D2: DIODE-SOD123; SOD123
D4, D7: PTR1PAD1-13; P1-13
F1: FUSE; C1812
IC1: AD8603UJ; SOT23-5
ICSP: PINHD-2X3; 2X03
IO12, IO13: PTR1PAD1-13; P1-13
JMP1: NM; R0402
Q1: CX2520SB; QUARTZ
R1, R2: 22; R0603
R3: 1M; R0603
R4, R5: 10k; R0603
R7, R8, R9: 10k 0.1%; R0603
R11: 13 0.1%; R2010
SUPPLY: PINHD-1X3; 1X03
SW1: B3U-1000P
TH_SIG: 734120110
U1: ATMEGA32U4-AU; QFP80P1200X1200X120-44N
U3: LTC2462IMSPBF; SOP65P490X110-12N
U4: LTC1655CS8PBF; SOIC127P600X175-8N
U$1: ADM7150; SO8
U$2: LT3092; SOT-223
U$3: GND_PAD
USB: 47346-0001; MOLEX_47346-0001
V1, V2: VARISTORCN0603; CT/CN0603

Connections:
+5V: C5.1, C10.1, C11.1, C12.1, C17.1, D2.C, IC1.5 (+VS), ICSP.2, R4.2, U1.2 (UVCC), U1.14 (VCC_2), U1.24 (AVCC_2), U1.34 (VCC), U1.44 (AVCC), U3.12 (VCC), U4.8 (VCC), U$1.2 (VOUT)
CLK: ICSP.3, U1.9 (PB1), U3.5 (SCK), U4.1 (CLK)
CS_ADC: U1.30 (PB6), U3.3 (~CS)
CS_CELL_TEMP: U1.31 (PC6)
CS_DAC: U1.27 (PD7), U4.3 (~CS/LD)
D+: R2.2, U1.4 (D+), V1.1
D-: R1.2, U1.3 (D-), V2.1
GND: ANALOG_I/O.6, ANALOG_I/O.7, ANALOG_I/O.8, ANALOG_I/O.9, C1.2, C2.2, C3.1, C4.1, C5.2, C6.2, C7.1, C8.1, C9.1, C10.2, C11.2, C12.2, C13.2, C14.2, C15.2, C16.2, C17.2, D1.A, IC1.2 (-VS), ICSP.6, Q1.2 (GND), R5.2, R9.1, R11.1, SUPPLY.1, SW1.1, TH_SIG.S@1 (2), TH_SIG.S@2 (2), TH_SIG.S@3 (2), U1.5 (UGND), U1.15 (GND_2), U1.23 (GND_3), U1.35 (GND_4), U1.43 (GND), U3.7 (GND_2), U3.8 (REF-), U3.11 (GND), U4.5 (GND), U$1.4 (GND), U$3.P$1, USB.5, V1.2, V2.2
IN+: C16.1, R7.1, R9.2, U3.9 (IN+)
IN-: ANALOG_I/O.5, C15.1, JMP1.1, R8.1, U3.10 (IN-)
MISO: ICSP.1, U1.11 (PB3), U3.6 (SDO)
MOSI: ICSP.4, U1.10 (PB2), U3.4 (SDI), U4.2 (DIN)
unnamed: F1.2 (XTAL2), USB.1
unnamed: R1.1, USB.2
unnamed: R2.1, USB.3
unnamed: U4.7 (VOUT), U$2.SET
unnamed: C8.2, U1.42 (AREF)
unnamed: C9.2, U1.6 (UCAP)
unnamed: R5.1, U1.33 (PE2)
unnamed: IO13.TP, U1.32 (PC7)
unnamed: D7.TP, U1.1 (PE6)
unnamed: C13.1, U3.2 (COMP)
unnamed: C14.1, R7.2, R8.2, U3.1 (REFOUT)
unnamed: D4.TP, U1.25 (PD4)
unnamed: IC1.1 (OUT), IC1.4 (IN-), TH_SIG.1
unnamed: IC1.3 (IN+), JMP1.2
unnamed: R11.2, U$2.OUT1, U$2.OUT2
unnamed: IO12.TP, U1.26 (PD6)
unnamed: C6.1, U$1.5 (RSEN), U$1.6 (REF)
unnamed: C7.2, U$1.1 (VREG)
unnamed: C2.1, U$1.3 (BYP)
RESET: D2.A, ICSP.5, R4.1, SW1.2, U1.13 (~RESET)
R_HEAT: ANALOG_I/O.3, ANALOG_I/O.4, U$2.IN
VCC: ANALOG_I/O.1, ANALOG_I/O.2, C1.1, D1.C, SUPPLY.2, SUPPLY.3, U$1.7 (EN), U$1.8 (VIN)
V_USB: F1.1 (XTAL1), U1.7 (VBUS)
XTAL1: C4.2, Q1.3 (XTAL2), R3.1, U1.17 (XTAL1)
XTAL2: C3.2, Q1.1 (XTAL1), R3.2, U1.16 (XTAL2)

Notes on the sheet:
Voltage regulation
XTAL
Digital
Reset and ICSP
Input / Output
Power stage
Analog-to-Digital Conversion
Temperature monitor
J. Rutkowski

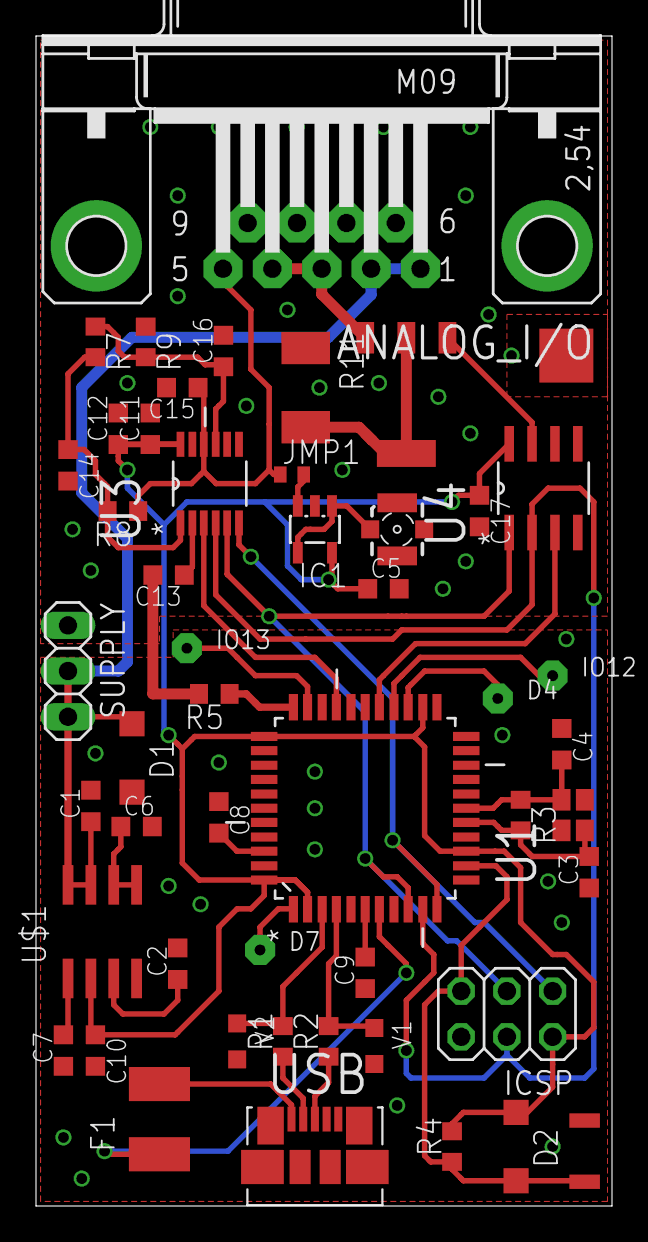
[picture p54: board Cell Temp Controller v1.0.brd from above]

Board: 2 copper layers, 32.0 x 65.0 mm, 50 parts (0 on the bottom side), 36 nets.

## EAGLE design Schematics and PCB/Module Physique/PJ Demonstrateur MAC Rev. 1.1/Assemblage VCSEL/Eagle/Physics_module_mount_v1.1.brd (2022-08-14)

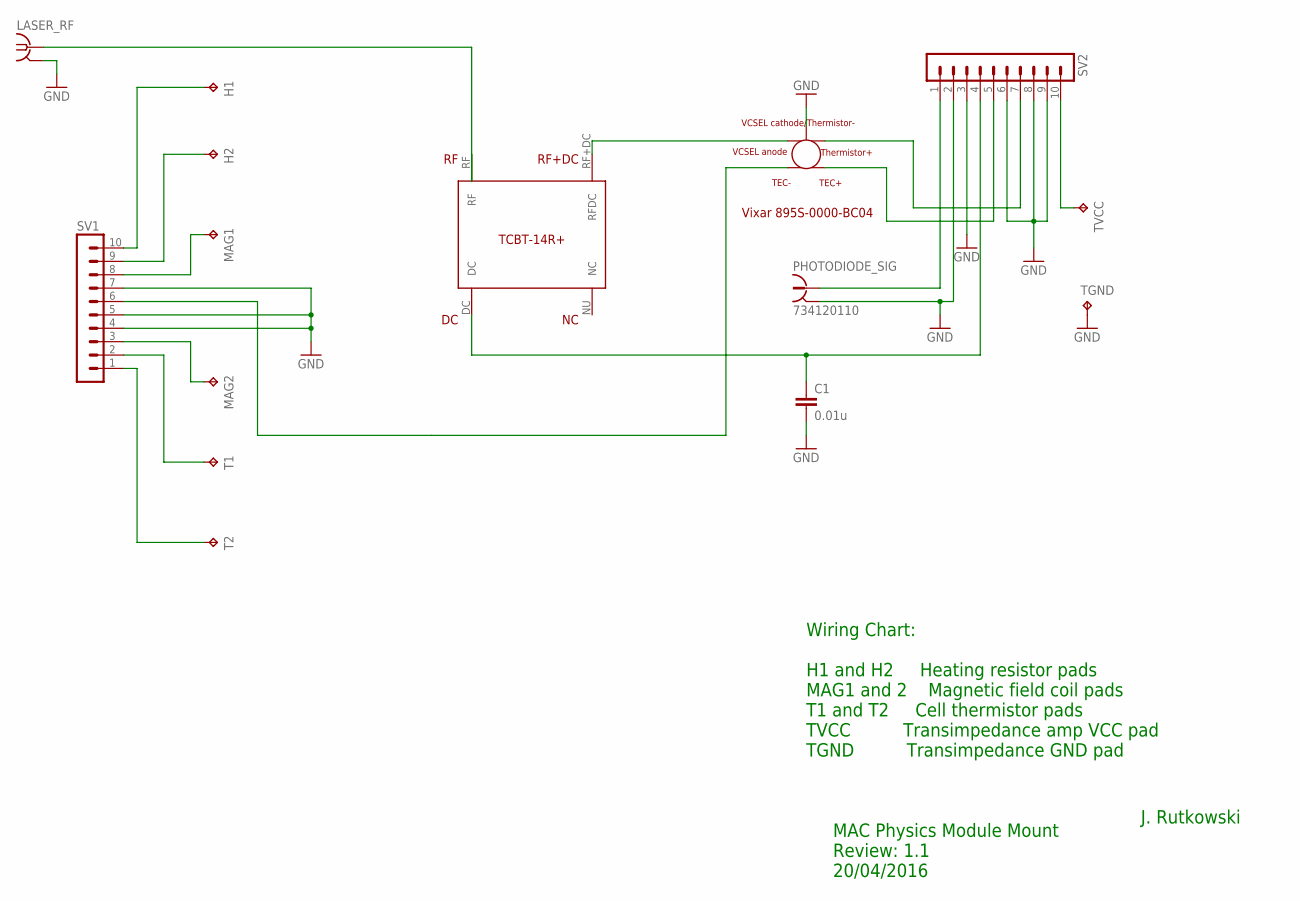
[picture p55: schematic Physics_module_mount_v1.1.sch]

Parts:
C1: 0.01u; C0603K
H1, H2: TPPAD1-13; P1-13
LASER_RF: SMA-142-0711-871/876; J502-ND-142-0711-871/876
MAG1, MAG2: TPPAD1-13; P1-13
PHOTODIODE_SIG: 734120110
Q1: VIXAR_895NM_VCSEL_TO46_6PIN; TO45_THT_SMD
SV1, SV2: MA10-1
T1, T2: TPPAD1-13; P1-13
TGND: TPPAD1-13; P1-13
TVCC: TPPAD1-13; P1-13
U1: TCBT-14+; TCBT_14_PAC

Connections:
GND: C1.2, LASER_RF.G@1 (2), LASER_RF.G@2 (2), LASER_RF.G@3 (2), LASER_RF.G@4 (2), PHOTODIODE_SIG.S@1 (2), PHOTODIODE_SIG.S@2 (2), PHOTODIODE_SIG.S@3 (2), Q1.LD_CATHODE_THERM (VCSEL_CATHODE/THERMISTOR-/CASE), SV1.4, SV1.5, SV1.7, SV2.2, SV2.3, SV2.6, SV2.8, SV2.9, TGND.TP
unnamed: H1.TP, SV1.10
unnamed: H2.TP, SV1.9
unnamed: MAG1.TP, SV1.8
unnamed: PHOTODIODE_SIG.1, SV2.1
unnamed: SV1.2, T1.TP
unnamed: SV1.1, T2.TP
unnamed: SV2.10, TVCC.TP
unnamed: LASER_RF.1, U1.RF
unnamed: Q1.LD_ANODE (VCSEL_ANODE), U1.RF+DC (RFDC)
unnamed: C1.1, SV2.4, U1.DC
unnamed: Q1.THERMISTOR (THERMISTOR+), SV2.7
unnamed: Q1.TEC+, SV2.5
unnamed: Q1.TEC-, SV1.6
unnamed: MAG2.TP, SV1.3

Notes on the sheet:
MAC Physics Module Mount Review: 1.1 20/04/2016
J. Rutkowski
Wiring Chart: H1 and H2 Heating resistor pads MAG1 and 2 Magnetic field coil pads T1 and T2 Cell thermistor pads TVCC Transimpedance amp VCC pad TGND Transimpedance GND pad

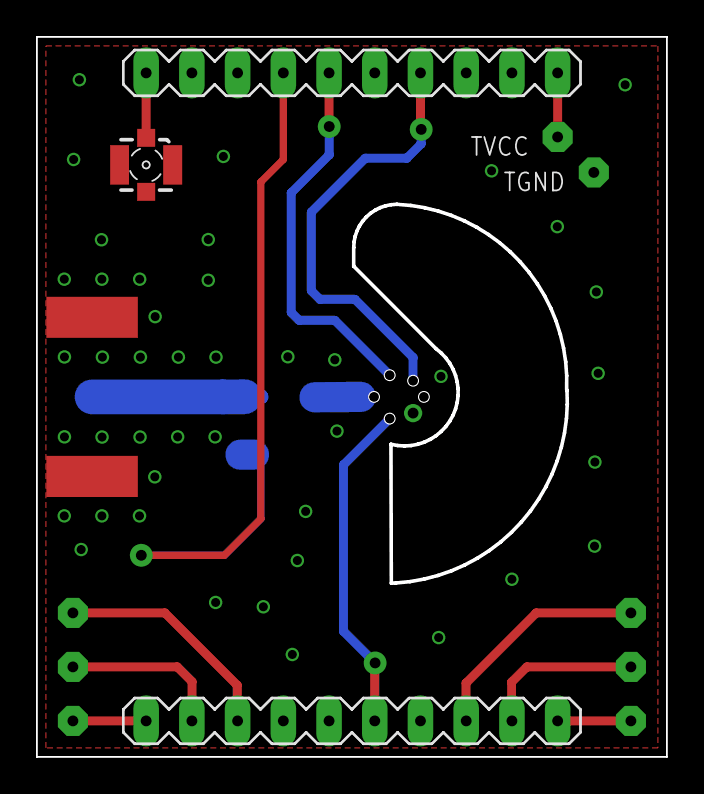
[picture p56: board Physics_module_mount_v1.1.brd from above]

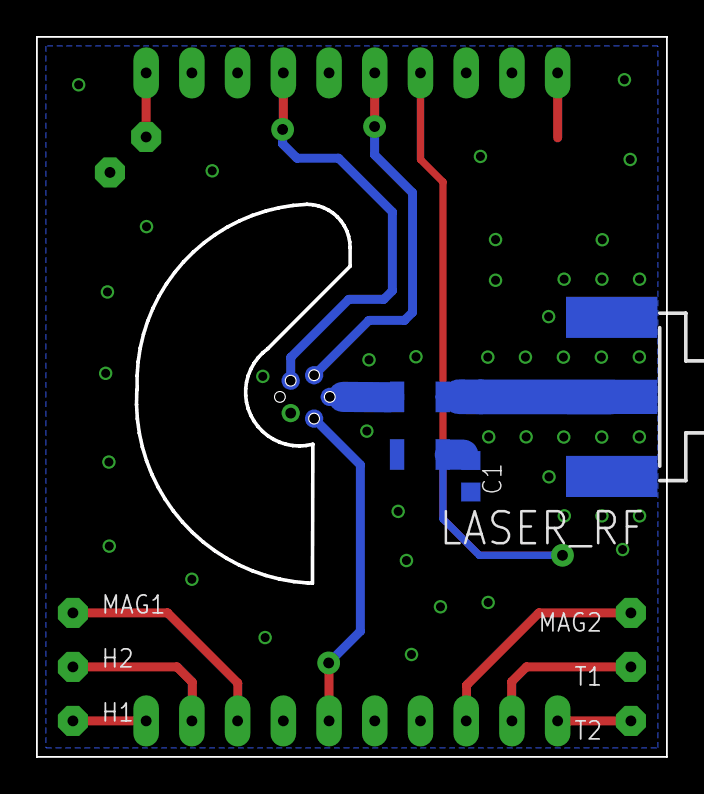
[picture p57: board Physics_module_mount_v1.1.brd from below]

Board: 2 copper layers, 35.0 x 40.0 mm, 15 parts (10 on the bottom side), 15 nets.

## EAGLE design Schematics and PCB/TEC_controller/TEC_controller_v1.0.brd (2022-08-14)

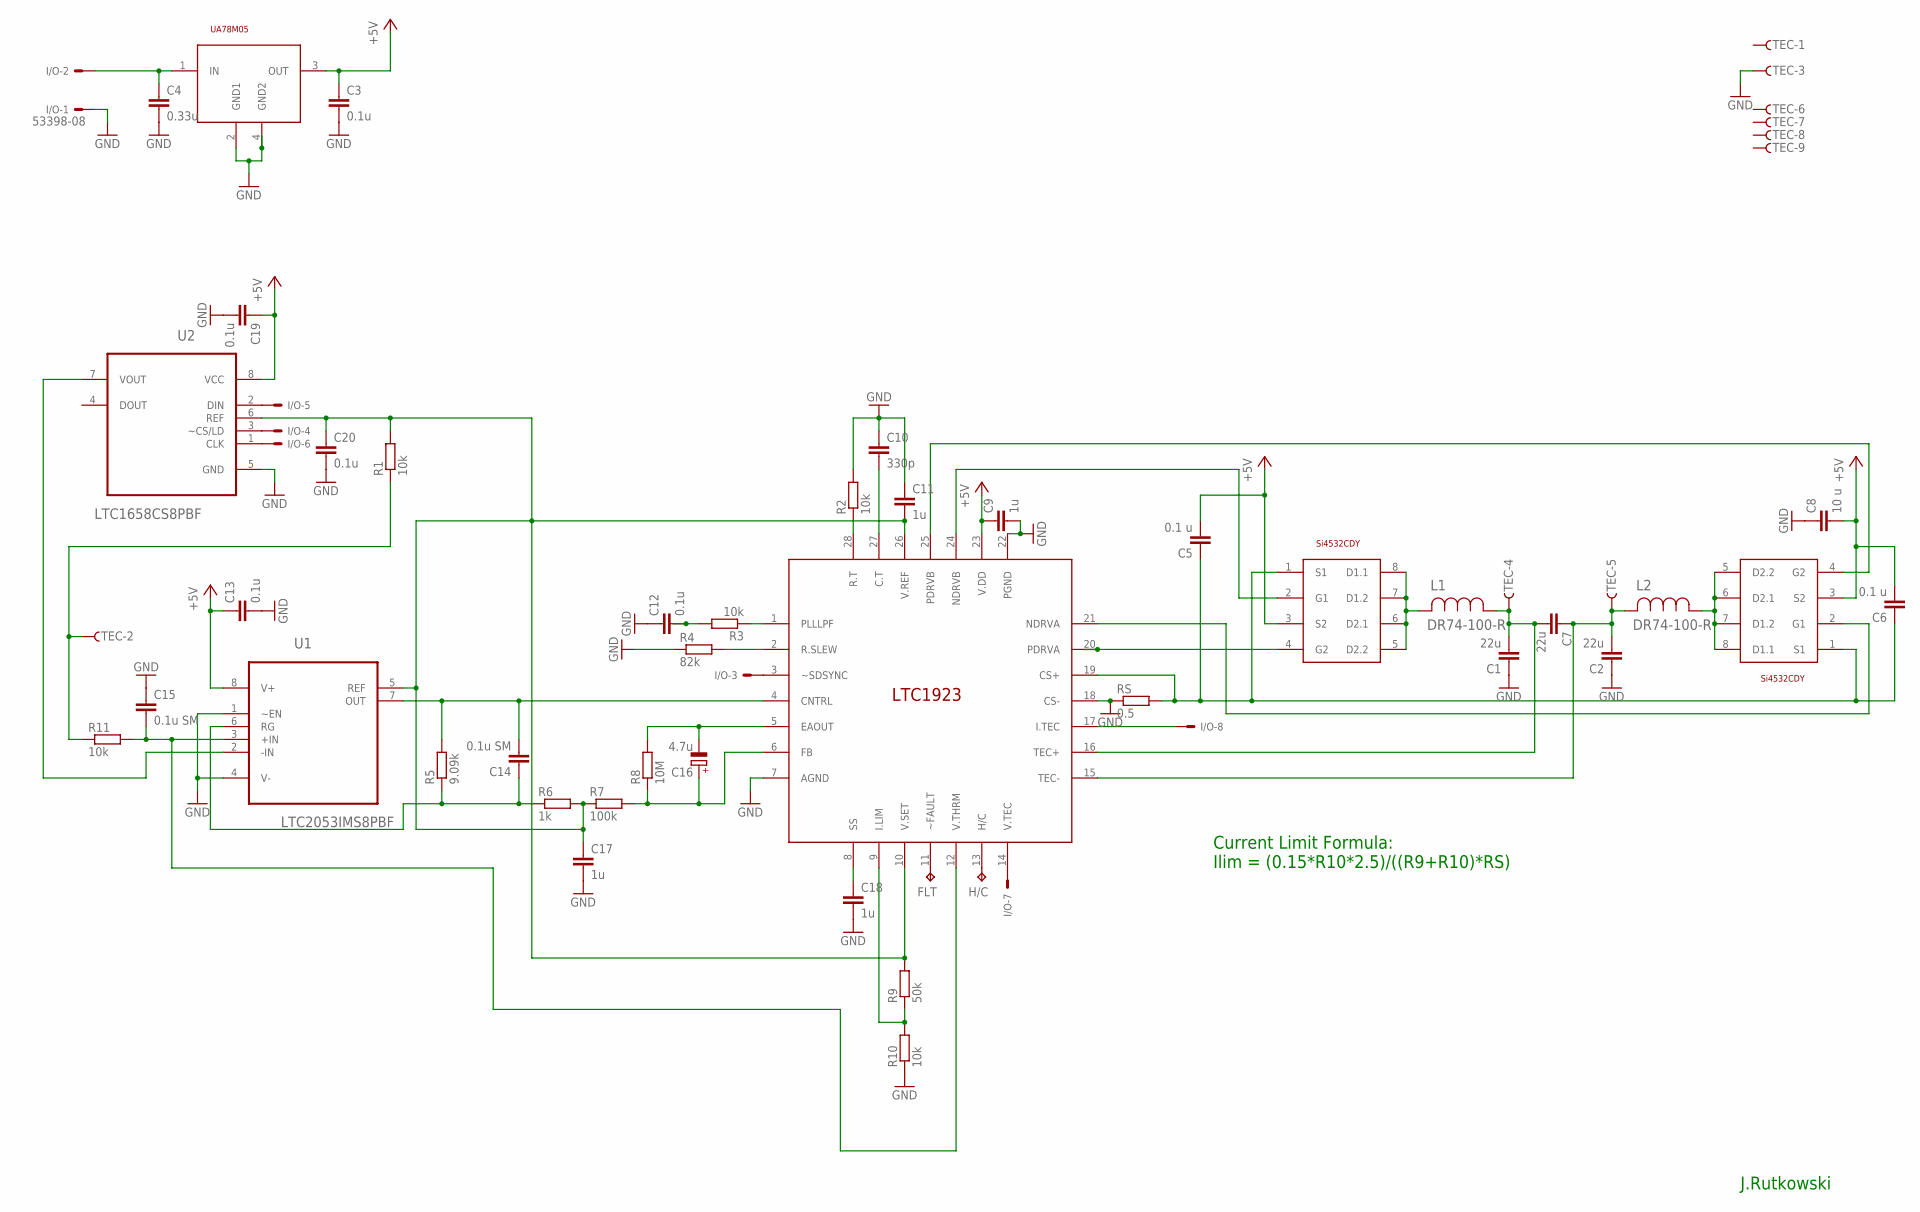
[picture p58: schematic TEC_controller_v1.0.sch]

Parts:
C1, C2, C7: 22u; C1210K
C3: 0.1u; C0805K
C4: 0.33u; C0805K
C5, C6: 0.1 u; C0805K
C8: 10 u; C1206K
C9, C11, C17, C18: 1u; C0603K
C10: 330p; C0603K
C12, C19, C20: 0.1u; C0603K
C13: 0.1u; C0603
C14, C15: 0.1u SM; C1210
C16: 4.7u; A/3216-18W
FLT: TPTP17SQ; TP17SQ
H/C: TPTP17SQ; TP17SQ
I/O: 53398-08
L1, L2: DR74-100-R; INDM7676X435N
R1, R2, R3, R10, R11: 10k; R0603
R4: 82k; R0603
R5: 9.09k; R0603
R6: 1k; R0603
R7: 100k; R0603
R8: 10M; R0603
R9: 50k; R0603
RS: 0.5; R1206
TEC: F09HPS; F09HP
U1: LTC2053IMS8PBF; SOP65P490X110-8N
U2: LTC1658CS8PBF; SOIC127P600X175-8N
U$1: LTC1923; SSOP28
U$2, U$3: SI4532CDY; SOIC127P600X175-8N
U$6: UA78M05; SOT-223

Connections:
+5V: C3.1, C5.2, C6.2, C8.2, C9.1, C13.1, C19.1, U1.8 (V+), U2.8 (VCC), U$1.23 (V.DD), U$2.3 (S2), U$3.3 (S2), U$6.3 (OUT)
GND: C1.1, C2.1, C3.2, C4.2, C8.1, C9.2, C10.1, C11.1, C12.1, C13.2, C15.1, C17.2, C18.2, C19.2, C20.2, I/O.1, R2.2, R4.1, R10.1, RS.1, TEC.3, U1.1 (~EN), U1.4 (V-), U2.5 (GND), U$1.7 (AGND), U$1.18 (CS-), U$1.22 (PGND), U$6.2 (GND1), U$6.4 (GND2)
unnamed: U$1.20 (PDRVA), U$2.4 (G2)
unnamed: C4.1, I/O.2, U$6.1 (IN)
unnamed: U$1.24 (NDRVB), U$2.2 (G1)
unnamed: L1.2, U$2.5 (D2.2), U$2.6 (D2.1), U$2.7 (D1.2), U$2.8 (D1.1)
unnamed: C1.2, C7.2, L1.1, TEC.4, U$1.16 (TEC+)
unnamed: L2.1, U$3.5 (D2.2), U$3.6 (D2.1), U$3.7 (D1.2), U$3.8 (D1.1)
unnamed: C5.1, C6.1, RS.2, U$1.19 (CS+), U$2.1 (S1), U$3.1 (S1)
unnamed: U$1.21 (NDRVA), U$3.2 (G1)
unnamed: C2.2, C7.1, L2.2, TEC.5, U$1.15 (TEC-)
unnamed: U$1.25 (PDRVB), U$3.4 (G2)
unnamed: I/O.4, U2.3 (~CS/LD)
unnamed: R2.1, U$1.28 (R.T)
unnamed: I/O.8, U$1.17 (I.TEC)
unnamed: C10.2, U$1.27 (C.T)
unnamed: I/O.7, U$1.14 (V.TEC)
unnamed: I/O.3, U$1.3 (~SDSYNC)
unnamed: I/O.5, U2.2 (DIN)
unnamed: I/O.6, U2.1 (CLK)
unnamed: H/C.TP, U$1.13 (H/C)
unnamed: R3.1, U$1.1 (PLLLPF)
unnamed: C12.2, R3.2
unnamed: R4.2, U$1.2 (R.SLEW)
unnamed: C14.2, R5.2, U1.7 (OUT), U$1.4 (CNTRL)
unnamed: C14.1, R5.1, R6.1, U1.6 (RG)
unnamed: FLT.TP, U$1.11 (~FAULT)
unnamed: C18.1, U$1.8 (SS)
unnamed: C15.2, R11.2, U1.3 (+IN), U$1.12 (V.THRM)
unnamed: C16.+, R7.2, R8.1, U$1.6 (FB)
unnamed: C16.-, R8.2, U$1.5 (EAOUT)
unnamed: R9.1, R10.2, U$1.9 (I.LIM)
unnamed: R1.1, R11.1, TEC.2
unnamed: U1.2 (-IN), U2.7 (VOUT)
unnamed: C11.2, C17.1, C20.1, R1.2, R6.2, R7.1, R9.2, U1.5 (REF), U2.6 (REF), U$1.10 (V.SET), U$1.26 (V.REF)

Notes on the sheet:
J.Rutkowski
Current Limit Formula: Ilim = (0.15*R10*2.5)/((R9+R10)*RS)

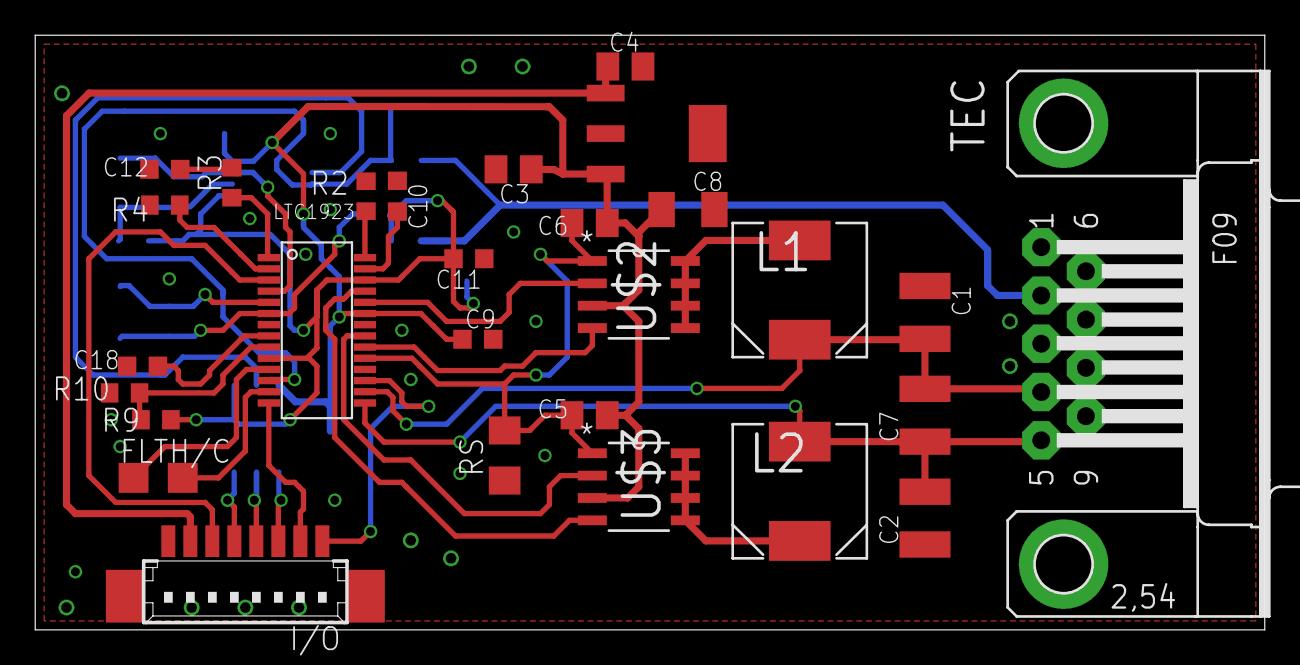
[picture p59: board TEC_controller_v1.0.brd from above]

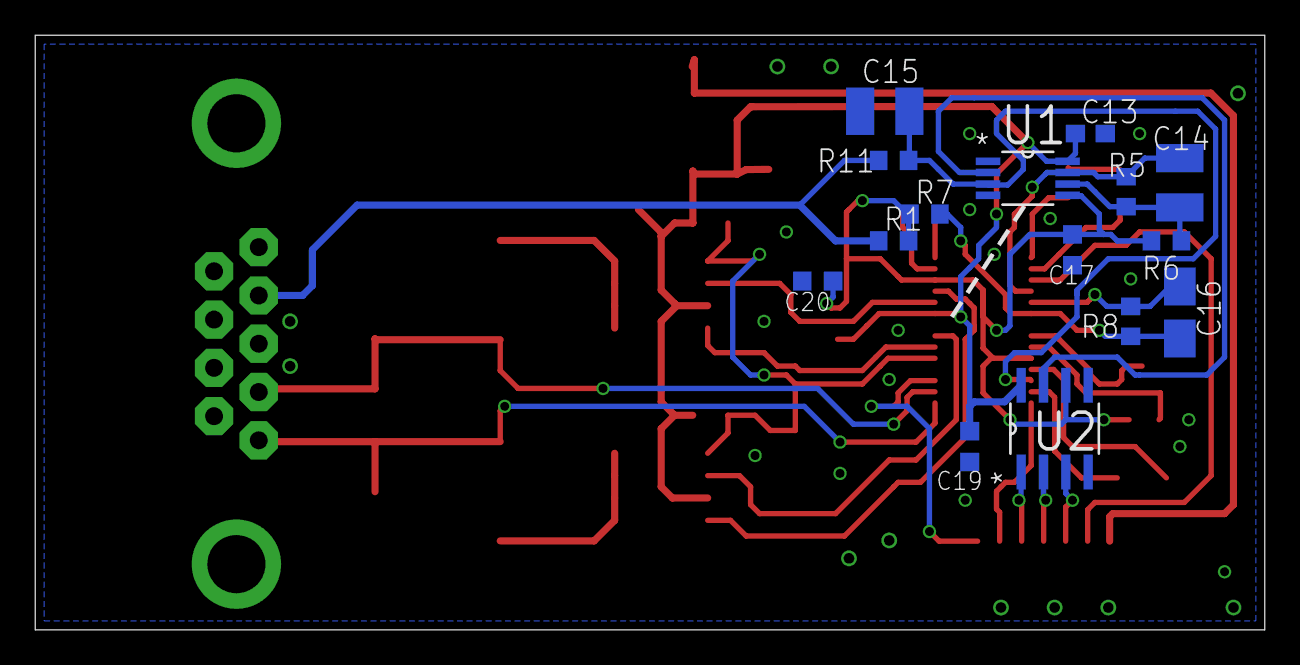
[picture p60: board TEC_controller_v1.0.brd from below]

Board: 2 copper layers, 69.8 x 33.8 mm, 44 parts (15 on the bottom side), 35 nets.

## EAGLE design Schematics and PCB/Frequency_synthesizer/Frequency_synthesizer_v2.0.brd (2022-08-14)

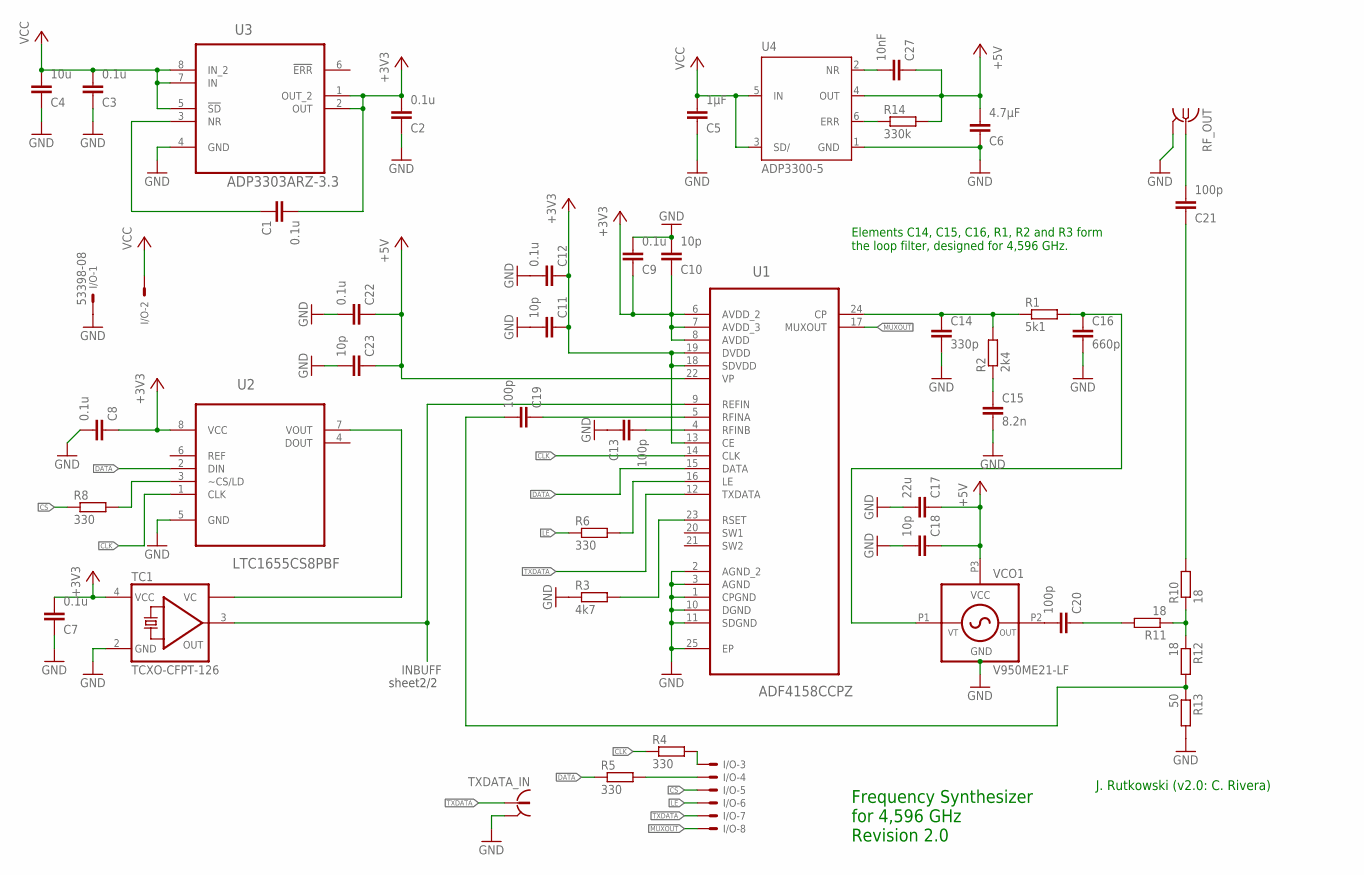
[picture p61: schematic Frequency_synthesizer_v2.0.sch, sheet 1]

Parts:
C1, C2, C3, C7, C8, C9, C12, C22: 0.1u; C0603K
C4: 10u; C0805K
C5: 1µF; C0603K
C6: 4.7µF; C0603K
C10, C11, C18, C23: 10p; C0603K
C13, C19, C20, C21: 100p; C0402
C14: 330p; C0603K
C15: 8.2n; C0603K
C16: 660p; C0603K
C17: 22u; C0805
C27: 10nF; C0603K
I/O: 53398-08
R1: 5k1; R0603
R2: 2k4; R0603
R3: 4k7; R0603
R4, R5, R6, R8: 330; R0603
R10, R11, R12: 18; R0402
R13: 50; R0402
R14: 330k; R0603
RF_OUT: SMA-142-0711-871/876; J502-ND-142-0711-871/876
TC1: TCXO-CFPT-126; 7.0X5.0-4-PAD
TXDATA_IN: 734120110
U1: ADF4158CCPZ; QFN50P400X400X80-25N
U2: LTC1655CS8PBF; SOIC127P600X175-8N
U3: ADP3303ARZ-3.3; SOIC127P600X175-8N
U4: ADP3300-5; SOT23-6
VCO1: V950ME21-LF; MINI-14S

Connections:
+3V3: C1.1, C2.1, C7.1, C8.2, C9.2, C10.2, C11.2, C12.2, TC1.4 (VCC), U1.6 (AVDD_2), U1.7 (AVDD_3), U1.8 (AVDD), U1.13 (CE), U1.18 (SDVDD), U1.19 (DVDD), U2.8 (VCC), U3.1 (OUT_2), U3.2 (OUT); also elsewhere on the board
+5V: C6.1, C17.2, C18.2, C22.2, C23.2, C27.2, R14.2, U1.22 (VP), U4.4 (OUT), VCO1.P3 (VCC)
CLK: R4.1, U1.14 (CLK), U2.1 (CLK)
CS: I/O.5, R8.1
DATA: R5.1, U1.15 (DATA), U2.2 (DIN)
GND: C2.2, C3.2, C4.2, C5.2, C6.2, C7.2, C8.1, C9.1, C10.1, C11.1, C12.1, C13.2, C14.2, C15.2, C16.2, C17.1, C18.1, C22.1, C23.1, I/O.1, R3.1, R13.2, RF_OUT.G@1 (2), RF_OUT.G@2 (2), RF_OUT.G@3 (2), RF_OUT.G@4 (2), TC1.2 (GND), TXDATA_IN.S@1 (2), TXDATA_IN.S@2 (2), TXDATA_IN.S@3 (2), U1.1 (CPGND), U1.2 (AGND_2), U1.3 (AGND), U1.10 (DGND), U1.11 (SDGND), U1.25 (EP), U2.5 (GND), U3.4 (GND), U4.1 (GND), VCO1.S1, VCO1.S2, VCO1.S3, VCO1.S4, VCO1.S5, VCO1.S6, VCO1.S7, VCO1.S8, VCO1.S9, VCO1.S10, VCO1.S11; also elsewhere on the board
INBUFF: TC1.3 (OUT), U1.9 (REFIN); also elsewhere on the board
LE: I/O.6, R6.1
MUXOUT: I/O.8, U1.17 (MUXOUT)
unnamed: C14.1, R1.1, R2.2, U1.24 (CP)
unnamed: C16.1, R1.2, VCO1.P1 (VT)
unnamed: C1.2, U3.3 (NR)
unnamed: C15.1, R2.1
unnamed: C13.1, U1.4 (RFINB)
unnamed: R8.2, U2.3 (~CS/LD)
unnamed: I/O.4, R5.2
unnamed: I/O.3, R4.2
unnamed: R14.1, U4.6 (ERR)
unnamed: TC1.1 (VC), U2.7 (VOUT)
unnamed: R6.2, U1.16 (LE)
unnamed: R3.2, U1.23 (RSET)
unnamed: C20.1, VCO1.P2 (OUT)
unnamed: C20.2, R11.2
unnamed: R10.1, R11.1, R12.1
unnamed: C19.1, R12.2, R13.1
unnamed: C21.2, R10.2
unnamed: C21.1, RF_OUT.1
unnamed: C19.2, U1.5 (RFINA)
unnamed: C27.1, U4.2 (NR)
TXDATA: I/O.7, TXDATA_IN.1, U1.12 (TXDATA)
VCC: C3.1, C4.1, C5.1, I/O.2, U3.5 (!SD), U3.7 (IN), U3.8 (IN_2), U4.3 (SD/), U4.5 (IN)

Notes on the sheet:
J. Rutkowski (v2.0: C. Rivera)
Elements C14, C15, C16, R1, R2 and R3 form the loop filter, designed for 4,596 GHz.
Frequency Synthesizer for 4,596 GHz Revision 2.0
sheet2/2

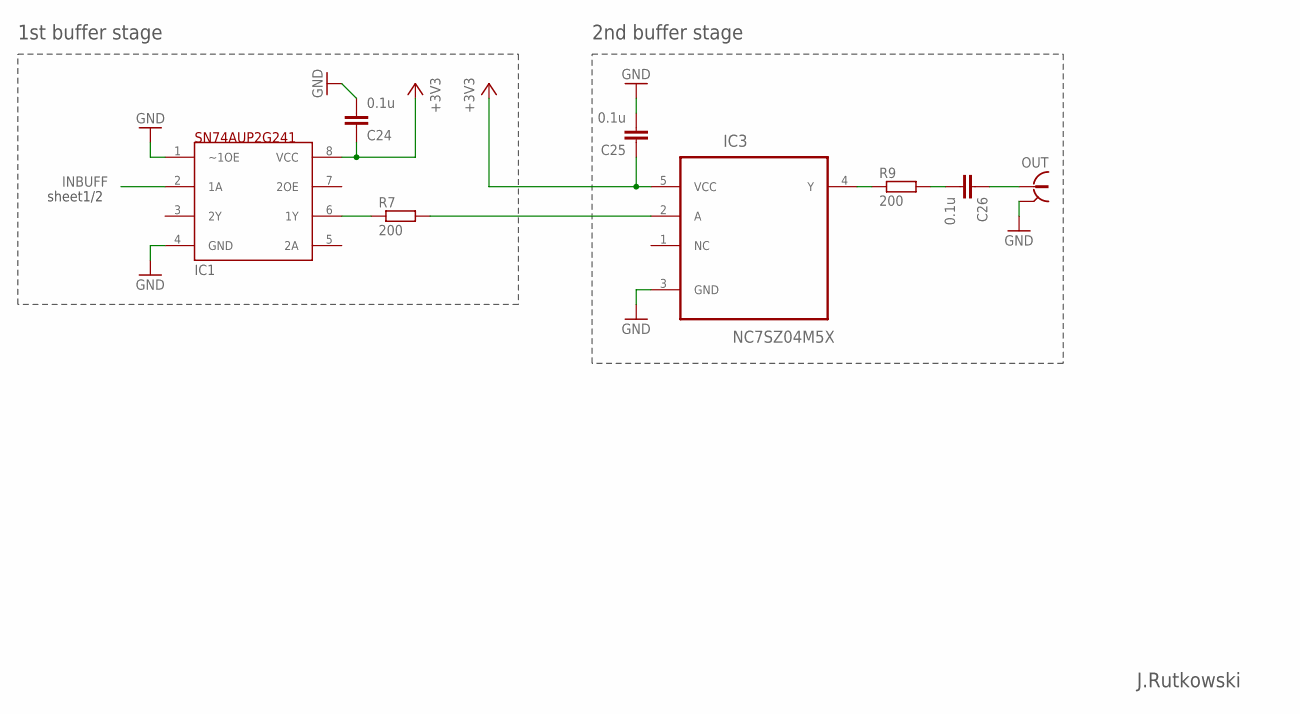
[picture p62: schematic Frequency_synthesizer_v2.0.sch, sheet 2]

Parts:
C24, C25, C26: 0.1u; C0603K
IC1: SN74AUP2G241; DCU_(R-PDSO-G8)
IC3: NC7SZ04M5X; SOT95P280X145-5N
OUT: 734120110
R7, R9: 200; R0603

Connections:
+3V3: C24.2, C25.2, IC1.8 (VCC), IC3.5 (VCC); also elsewhere on the board
GND: C24.1, C25.1, IC1.1 (~1OE), IC1.4 (GND), IC3.3 (GND), OUT.S@1 (2), OUT.S@2 (2), OUT.S@3 (2); also elsewhere on the board
INBUFF: IC1.2 (1A); also elsewhere on the board
unnamed: IC1.6 (1Y), R7.1
unnamed: IC3.2 (A), R7.2
unnamed: IC3.4 (Y), R9.1
unnamed: C26.1, R9.2
unnamed: C26.2, OUT.1

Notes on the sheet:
1st buffer stage
J.Rutkowski
2nd buffer stage
sheet1/2

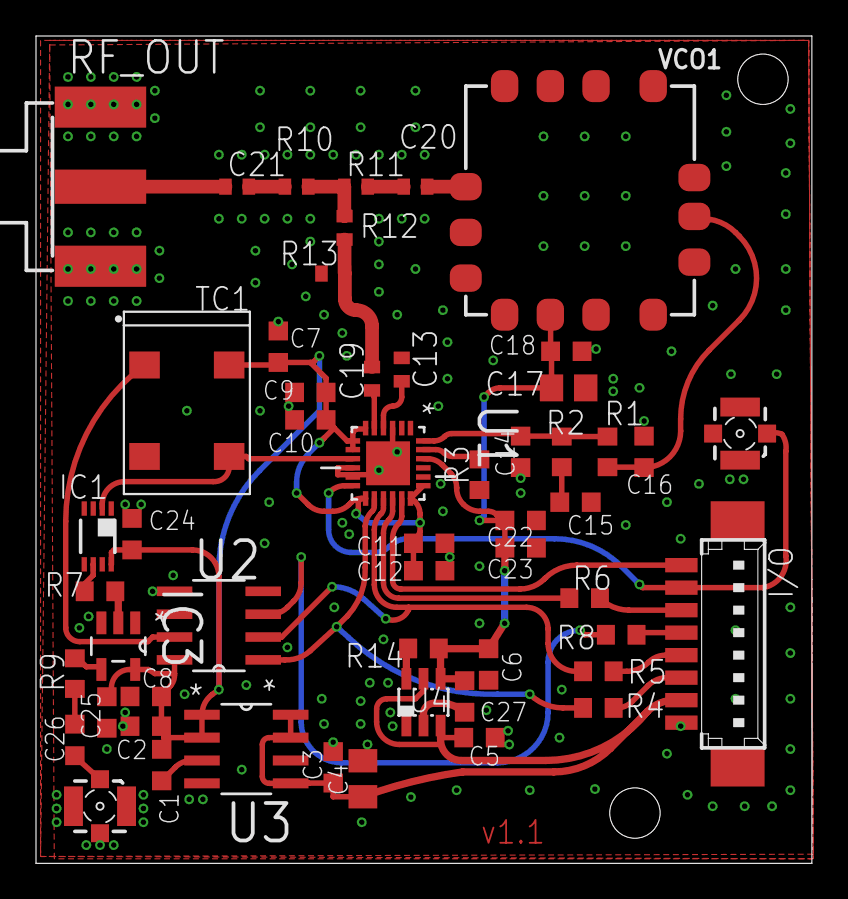
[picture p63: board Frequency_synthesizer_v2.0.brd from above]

Board: 2 copper layers, 43.1 x 46.0 mm, 53 parts (0 on the bottom side), 36 nets.

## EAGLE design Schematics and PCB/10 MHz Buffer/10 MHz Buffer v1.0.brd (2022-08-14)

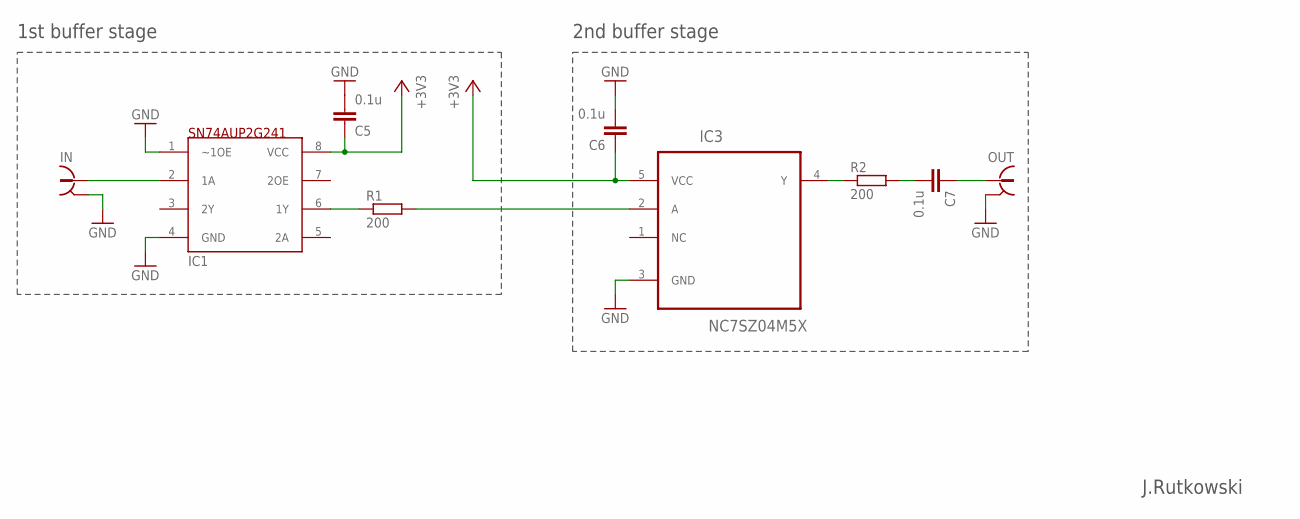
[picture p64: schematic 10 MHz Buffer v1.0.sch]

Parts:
C5, C6, C7: 0.1u; C0603K
IC1: SN74AUP2G241; DCU_(R-PDSO-G8)
IC3: NC7SZ04M5X; SOT95P280X145-5N
IN: 734120110
OUT: 734120110
R1, R2: 200; R0603

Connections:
+3V3: C5.2, C6.2, IC1.8 (VCC), IC3.5 (VCC)
GND: C5.1, C6.1, IC1.1 (~1OE), IC1.4 (GND), IC3.3 (GND), IN.S@1 (2), IN.S@2 (2), IN.S@3 (2), OUT.S@1 (2), OUT.S@2 (2), OUT.S@3 (2)
unnamed: IC1.2 (1A), IN.1
unnamed: IC1.6 (1Y), R1.1
unnamed: IC3.2 (A), R1.2
unnamed: IC3.4 (Y), R2.1
unnamed: C7.1, R2.2
unnamed: C7.2, OUT.1

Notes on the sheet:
1st buffer stage
J.Rutkowski
2nd buffer stage


Board: 2 copper layers, 33.0 x 16.2 mm, 9 parts (0 on the bottom side), 8 nets.

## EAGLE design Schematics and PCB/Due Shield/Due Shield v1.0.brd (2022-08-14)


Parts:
BOARD_SUPP: W237-102
C1, C2: 1u; C0805K
C3: 0.1u; C0805K
CON1: CON20
PCB1: ARDUINO_DUE
POWER_JACK: FC681465P
R1: 10k; R0603
R2: 750k; R0603
R3, R4: 62k; R0603
R6, R7: 100k; R0603
SW1: 1101M2S3CQE2
U$1: B3U-1000
U$2: ADP7105; SO8
X1, X2: BU-SMA-V

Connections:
CLK: CON1.7, PCB1.SCK
CS_CELL_TEMP: CON1.14
CS_DAC_SYNTH: CON1.11, PCB1.2
CS_DAC_TEC: CON1.16, PCB1.7
CS_MAG_FIELD: CON1.2, PCB1.8
CS_PD_ADC: CON1.8
CS_VCSEL: CON1.19, PCB1.5
DATA: CON1.3, PCB1.MOSI
DATA_ADC: CON1.6
GND: BOARD_SUPP.2, C1.1, C2.2, CON1.1, CON1.5, CON1.9, CON1.10, CON1.20, PCB1.GND, PCB1.GND., PCB1.GND.., POWER_JACK.2 (GND1), POWER_JACK.3 (GND2), R1.1, R3.1, R6.1, SW1.3, U$2.3 (GND), U$2.6 (GND2), X1.2, X1.3 (2), X1.4 (2), X1.5 (2), X2.2, X2.3 (2), X2.4 (2), X2.5 (2)
LE: CON1.13, PCB1.3
LOCK_OFF: PCB1.9, R1.2, U$1.1, U$1.2
MISO: CON1.12
MISO_ADC: CON1.4
MUXOUT: CON1.17
unnamed: PCB1.3.3V, U$1.3, U$1.4
unnamed: PCB1.A0, X1.1, X2.1
unnamed: BOARD_SUPP.1, C2.1, C3.1, R2.2, U$2.1 (VOUT)
unnamed: R2.1, R3.2, R4.1, U$2.2 (SEN/ADJ)
unnamed: C1.2, POWER_JACK.1 (V+), SW1.1, U$2.8 (VIN)
unnamed: C3.2, R4.2
unnamed: R6.2, R7.2, U$2.5 (EN/UVLO)
unnamed: R7.1, SW1.2
TEC_ON/OFF: CON1.18, PCB1.6
TXDATA: CON1.15, PCB1.4

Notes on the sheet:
IDC Pinout
Due interface
Board Power Supply (16 V out)
J.Rutkowski
Due Shield for MAC test board interconnection and "Wall-Wart" power supply distribution.

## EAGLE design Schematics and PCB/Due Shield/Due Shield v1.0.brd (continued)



Board: 2 copper layers, 53.3 x 105.4 mm, 18 parts (10 on the bottom side), 19 nets.

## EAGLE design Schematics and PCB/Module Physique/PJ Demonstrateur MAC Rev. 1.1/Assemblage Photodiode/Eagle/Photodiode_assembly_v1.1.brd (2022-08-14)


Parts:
C1: 6p; C0805K
C2: 0.1u; C0805K
C3: 1u; C0805K
D1: TEMD5020; TEMD5020_OUTLINE
IC1: AD820R; SO8
R1: 220k; R0805
R2: 1k; R0805
SIG+: TPPAD1-13Y; P1-13Y
SIG_GND: TPPAD1-13Y; P1-13Y
TGND: TPPAD1-13Y; P1-13Y
TVCC: TPPAD1-13Y; P1-13Y

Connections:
+5V: C2.2, C3.2, IC1.7 (+VS), TVCC.TP
GND: C2.1, C3.1, D1.ANODE_BRD (ANODE_SYM), IC1.3 (IN+), IC1.4 (-VS), SIG_GND.TP, TGND.TP
unnamed: C1.1, D1.CATHODE_BRD (CATHODE), IC1.2 (IN-), R1.1
unnamed: C1.2, IC1.6 (OUT), R1.2, R2.1
unnamed: R2.2, SIG+.TP

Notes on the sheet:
Photodiode Assembly Review 1.1 21/04/2016
J. Rutkowski


Board: 2 copper layers, 29.0 x 29.0 mm, 11 parts (1 on the bottom side), 5 nets.

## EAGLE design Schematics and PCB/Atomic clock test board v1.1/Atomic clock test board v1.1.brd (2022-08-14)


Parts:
ADC_CON: 53047-06
C1, C4, C7, C13: 1u; C0603K
C2, C3, C8, C9, C10, C11: 0.1u; C0603K
C5, C6, C12: 10u; C0603K
CELL_TEMP_CONTR: 53398-08
CELL_TEMP_SUBD: F09HPS; F09HP
CON1: CON20
IC1, IC2: AD8603UJ; SOT23-5
ILD_EXT: 734120110
JMP1, JMP2: NM; R0402
MUXOUT: 734120110
PD_SIGNAL1, PD_SIGNAL2: 734120110
R1: 200 (0.1%); R0603
R2, R4: 100; R0603
R3: 10 (0.1%); R0603
R5, R6, R7, R8, R9, R10: 330; R0603
SUPPLY: W237-102
SYNTHESIZER: 53398-08
T1: MMBT3904LT1-NPN-SOT23-BEC; SOT23-BEC
TEC_CONTROLLER: 53398-08
TEC_SUB-D: M09HPS; M09HP
TP1: PTR1PAD1-13; P1-13
U1, U2: LTC1655CS8PBF; SOIC127P600X175-8N
U$1: MAC_MOUNT_V1; MAC_MOUNT_PAC_V1
U$2, U$4: AD8275; MSOP08
U$5: ADM7150; SO8
U$6, U$7, U$8: GND_PAD

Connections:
+5V: C2.2, C3.1, C5.1, C8.2, C9.1, C10.2, C11.2, IC1.5 (+VS), IC2.5 (+VS), T1.C, U1.8 (VCC), U2.8 (VCC), U$2.7 (+VS), U$4.7 (+VS), U$5.2 (VOUT)
CLK: ADC_CON.6, CELL_TEMP_CONTR.7, CON1.7, R7.1, R10.1, SYNTHESIZER.3, TEC_CONTROLLER.6
CS_CELL_TEMP: CELL_TEMP_CONTR.4, CON1.14
CS_DAC_SYNTH: CON1.11, SYNTHESIZER.5
CS_DAC_TEC: CON1.16, TEC_CONTROLLER.4
CS_MAG_FIELD: CON1.2, R9.1
CS_PD_ADC: ADC_CON.3, CON1.8
CS_VCSEL: CON1.19, R6.1
DATA: CELL_TEMP_CONTR.5, CON1.3, R5.1, R8.1, SYNTHESIZER.4, TEC_CONTROLLER.5
DATA_ADC: ADC_CON.4, CON1.6
GND: ADC_CON.1, C1.2, C2.1, C3.2, C4.2, C5.2, C6.2, C7.2, C8.1, C9.2, C10.1, C11.1, C12.1, C13.2, CELL_TEMP_CONTR.1, CELL_TEMP_SUBD.6, CELL_TEMP_SUBD.7, CELL_TEMP_SUBD.8, CELL_TEMP_SUBD.9, CON1.1, CON1.5, CON1.9, CON1.10, CON1.20, IC1.2 (-VS), IC2.2 (-VS), ILD_EXT.S@1 (2), ILD_EXT.S@2 (2), ILD_EXT.S@3 (2), MUXOUT.S@1 (2), MUXOUT.S@2 (2), MUXOUT.S@3 (2), PD_SIGNAL1.S@1 (2), PD_SIGNAL1.S@2 (2), PD_SIGNAL1.S@3 (2), PD_SIGNAL2.S@1 (2), PD_SIGNAL2.S@2 (2), PD_SIGNAL2.S@3 (2), SUPPLY.2, SYNTHESIZER.1, TEC_CONTROLLER.1, TEC_SUB-D.1, TEC_SUB-D.3, TEC_SUB-D.6, TEC_SUB-D.7, TEC_SUB-D.8, TEC_SUB-D.9, U1.5 (GND), U2.5 (GND), U$1.GND1, U$1.GND2, U$1.GND3, U$1.GND4, U$1.GND5, U$1.GND6, U$1.GND7, U$1.GND8, U$1.MAG_FIELD2, U$1.TH_CELL1, U$2.2 (-IN), U$2.4 (-VS), U$4.2 (-IN), U$4.4 (-VS), U$5.4 (GND), U$6.P$1, U$7.P$1, U$8.P$1
LE: CON1.13, SYNTHESIZER.6
MISO: CELL_TEMP_CONTR.6, CON1.12
MISO_ADC: ADC_CON.5, CON1.4
MUXOUT: CON1.17, MUXOUT.1, SYNTHESIZER.8
unnamed: C1.1, R2.2, U$2.3 (+IN)
unnamed: R1.2, U$2.5 (SENSE), U$2.6 (OUT)
unnamed: IC1.3 (IN+), JMP2.1, R1.1
unnamed: IC1.1 (OUT), IC1.4 (IN-), U$2.1 (REF1), U$2.8 (REF2)
unnamed: CELL_TEMP_SUBD.1, CELL_TEMP_SUBD.2, U$1.CELL_HEAT2 (CELL_HEATER2)
unnamed: R2.1, U1.7 (VOUT)
unnamed: T1.B, U$4.6 (OUT)
unnamed: R3.1, T1.E, U$4.5 (SENSE)
unnamed: IC2.1 (OUT), IC2.4 (IN-), U$4.1 (REF1), U$4.8 (REF2)
unnamed: C7.1, R4.2, U$4.3 (+IN)
unnamed: R4.1, U2.7 (VOUT)
unnamed: IC2.3 (IN+), R3.2, U$1.MAG_FIELD1
unnamed: R5.2, U1.2 (DIN)
unnamed: R6.2, U1.3 (~CS/LD)
unnamed: R7.2, U1.1 (CLK)
unnamed: R8.2, U2.2 (DIN)
unnamed: R9.2, U2.3 (~CS/LD)
unnamed: R10.2, U2.1 (CLK)
unnamed: PD_SIGNAL1.1, PD_SIGNAL2.1, U$1.PD+
unnamed: TEC_SUB-D.5, U$1.LD_TEC-
unnamed: TEC_SUB-D.4, U$1.LD_TEC+
unnamed: TEC_SUB-D.2, U$1.LD_TH+
unnamed: CELL_TEMP_SUBD.3, CELL_TEMP_SUBD.4, U$1.CELL_HEAT1 (CELL_HEATER1)
unnamed: JMP1.1, JMP2.2, U$1.LD_ANODE
unnamed: CELL_TEMP_SUBD.5, U$1.TH_CELL2
unnamed: ILD_EXT.1, JMP1.2
unnamed: C4.1, U$5.5 (RSEN), U$5.6 (REF)
unnamed: C12.2, U$5.1 (VREG)
unnamed: C13.1, U$5.3 (BYP)
TEC_ON/OFF: CON1.18, TEC_CONTROLLER.3
TXDATA: CON1.15, SYNTHESIZER.7
VCC: ADC_CON.2, C6.1, CELL_TEMP_CONTR.2, CELL_TEMP_CONTR.3, SUPPLY.1, SYNTHESIZER.2, TEC_CONTROLLER.2, TP1.TP, U$1.VCC, U$5.7 (EN), U$5.8 (VIN)

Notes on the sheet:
Digital I/O
Subassembly I/O
Voltage regulation
VCSEL Current Source
Magnetic Field Current Source
MAC Socket
J.Rutkowski


Board: 2 copper layers, 132.1 x 90.5 mm, 50 parts (0 on the bottom side), 47 nets.

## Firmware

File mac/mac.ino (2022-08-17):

#include <SPI.h>

// Added integral term to the CPT lock 
// Added d-part and serial interface for pid parameter input to the CPT lock part
// Adc 1V
// lock step
// Added D part to CPT lock
// new Laser Lock ONE put into ErrorDisplay ()
// Version 2.0 added DQI prefixes to interface
// Version after tidying up and adding the RF suppressor
// FSR ADC 256 mV
// Test of error signal with laser TEC modulation
// FM dev 1.67kHz

/* Updated by Carlos RIVERA, july 2022:
- Added visual controls to operate the demonstrator without console commands.
- Converted all machine units in the GUI (graph and controls) to physical units.
- Completely redesigned the "Control panel".
- Added the option to change the laser modulation width.
- Added the option to change the Quartz scan parameters (initial and final values).
- Added double function buttons to start/processes without relying on the physical button.
- Added Absorption Signal graph to monitor the output of the photodiode and not use an oscilloscope.
- Added titles and axis labels to all the graphs.
- Added "Maximum Absorption" graphic tool.
- Added servo loops lock state markers for Laser and Quartz graphs
- Added CPT signal graph
*/

const int CS_DAC_quartz = 2;                              // Set CS pins
const int CS_ADF4158 = 3;                                 
const int TXDATA = 4;
const int CS_VCSEL = 5;
const int TEC_on_off = 6;
const int CS_DAC_TEC = 7;
const int CS_mag = 8;
const int ButtonPin = 9;
const int ADC_DRDY = 11;
const int CS_ADC = 12;
const int Lock_trigger = 61;    //  CR: analog pin A7, apparently not connected to anything, only oscilloscope trigger purpose.

int laser_lock_step = 1;         // CR: Laser lock step
int lock_step_cpt = 1;           // CR: Quartz lock step
const int averages = 1;          // Number of averages before each laser lock step
int init_VCSEL_current = 30000;  // Laser current word after initial startup ->44564 (1.7 mA)
int quartz_init = 10000;   // Initial quartz dac word -1500 avec synthese j
int quartz_offset = 0;
float kp = 0.4;
float ki = 0.01;
float kd = 0;
float kpl = 0.7;
unsigned int scanStart = 24000;  //---------------------
unsigned int scanEnd;
unsigned int scanSamples = 300;

unsigned int scanQuartzStart=0;
unsigned int scanQuartzEnd = 41530;

unsigned int attenuator_word = 0;
unsigned int TEC_WORD = 8829;
unsigned int SweepModulationWidth = 1;
int RF_step = 30;

void setup() {
  pinMode(CS_ADF4158, OUTPUT);
  pinMode(Lock_trigger, OUTPUT);
  pinMode(TXDATA, OUTPUT);
  pinMode(CS_DAC_quartz, OUTPUT);
  pinMode(CS_DAC_TEC, OUTPUT);
  pinMode(TEC_on_off, OUTPUT);
  pinMode(CS_mag, OUTPUT);
  pinMode(CS_VCSEL, OUTPUT);
  pinMode(CS_ADC, OUTPUT);
  pinMode(ButtonPin, INPUT);
  pinMode(ADC_DRDY, INPUT);
  digitalWrite(TEC_on_off, LOW);                          // Sets CS pins high and others low at startup
  digitalWrite(CS_ADF4158, HIGH);
  digitalWrite(CS_DAC_quartz, HIGH);
  digitalWrite(CS_DAC_TEC, HIGH);
  digitalWrite(CS_mag, HIGH);
  digitalWrite(CS_VCSEL, HIGH);
  digitalWrite(CS_ADC, HIGH);
  digitalWrite(Lock_trigger, LOW);
  digitalWrite(TXDATA, LOW);
  
  SPI.begin();
  SPI.setClockDivider(SPI_CLOCK_DIV128);                // Lower the SPI transmision speed in case of long signal wires
  Serial.begin(115200);  
  print_title();
  print_menu();
  //analogWriteResolution(12);   // ???????? fonction pas défini
  //analogWrite(DAC1, attenuator_word);  // ???????? fonction pas défini

  // Set the magnetic field current and Quartz VCO at 0 by default:
  Show_CPT();
  return;
    //-------------initial value vcsel--------------erase this block if problem
   byte byte1 = (init_VCSEL_current >> 8);
   byte byte2 = (init_VCSEL_current & 0xff);
   digitalWrite(CS_VCSEL, LOW);
   SPI.transfer(byte1);                                 
   SPI.transfer(byte2);
   digitalWrite(CS_VCSEL, HIGH);
  //-------------------------------------------------
}

void loop(){                                              // Main loop
  while (!Serial.available());
  parseMenu(Serial.read());
}


/* -------------------------------------------------------- FUNCTION DECLARATIONS ----------------------------------------------- */
void parseMenu(char c){                                  // Switches between different menu options
  switch (c){
    case '0':
      ErrorDisplay();
      break;
    
    case '1':
      DAC_load(CS_DAC_quartz);
      break;
    
    case '2':
      Show_CPT();
      break;
    
    case '3':
      LaserLock();
      break;
      
    case '4':
      ADF4158_Reg_Write();
      break;
    
    case '5':
      TEC_DAC_load();
      break;
      
    case '6':
      TEC_on();
      break;
    
    case '7':
      TEC_off();
      break;

    case '8':
      DAC_load(CS_mag);
      break;

    case '9':
      DAC_load(CS_VCSEL);
      break;

    case 'a':
      setPidParams();
      break;

    case 'b':
      QuartzScan(scanQuartzStart,scanQuartzEnd);
      break;

    case 'c':
      set_synth_CPT();
      break;
      
    case 'i':
      setLaserLockParameters();
      break;

    case 'j':
      setQuartzLockParameters();
      break;

    case 'd':
      setAttenuatorWord();
      break;

    case 'l':
      NewLaserLock();
      break;

    case 'u':
      setLockStep();
      break;

    case 's':
      LaserScan(scanStart,scanEnd,scanSamples);
      break;

    case 't':
      LaserScanSetStart();
      break;

    case 'v':
      QuartzScanSetStart();
      break;
    
    case 'r':
      RFPowerScan();
      break;

    case 'z':
      SetTecWord();
      break;

    case 'w':
      SetSweepModulationWidth();
      break;
  }
}


void print_title() {                                     // Prints title        
  printDebug("***************************************************");
  printDebug("* Program Rev. 1.7 MAC demonstrator\t\t\t*");
  printDebug("* FEMTO-ST 2016-2022\t\t\t\t*");
  printDebug("*\t\t\t\t\t*");
  printDebug("* Software ver. 1.7  // July 2022\t\t\t*");
  printDebug("* Author: J. Rutkowski (v1.6 Benoit Dubois) (v1.7 Carlos RIVERA)\t*");
  printDebug("***************************************************");
  // printDebug("");
}


void print_menu() {                                      // Prints main menu.  
  return; //CR: Console is no longer used, only GUI controls
  printDebug("Menu:");
  printDebug("  0 - VCSEL startup and set to 1,7 mA");
  printDebug("  1 - [space] [decimal value] - Set quartz bias"); //Set PLL to 4.6 GHz");
  printDebug("  2 - Set values to show CPT signal");
  printDebug("  3 - Laser Lock ON ");                     
  printDebug("  4 [space] [decimal value] - Set individual PLL register");
  printDebug("  5 [space] [decimal value] - Set laser TEC setpoint");
  printDebug("  6 - TEC ON");
  printDebug("  7 - TEC OFF");
  printDebug("  8 - [space] [decimal value] - Set Mag field");
  printDebug("  9 - [space] [decimal value] - Set VCSEL current");
  printDebug("");
}

//case '1':
void DAC_load(int CS_pin) {                             // Loads data to LTC1655L 16-bit DAC through SPI, takes the CS pin as input
  unsigned int value = Serial.parseInt();               // Parses an int from the serial input
  byte byte1 = (value >> 8);   // byte1 (MSb) = 0x xxxx xxxx 0000 0000
  byte byte2 = (value & 0xff); // byte2 (LSb) = 0x 0000 0000 xxxx xxxx
  digitalWrite(CS_pin, LOW);
  SPI.transfer(byte1);                                  
  SPI.transfer(byte2);
  digitalWrite(CS_pin, HIGH);  // The DAC register loads the data from the shift register when CS/LD is pulled high.
  Serial.print("D DAC word: ");
  Serial.print(byte1, BIN);
  Serial.println(byte2, BIN);
}

void DAC_load(int CS_pin, unsigned int value) {          // Loads data to LTC1655L 16-bit DAC through SPI, takes the CS pin and value to load (uint) as input
   byte byte1 = (value >> 8);   
   byte byte2 = (value & 0xff); 
   digitalWrite(CS_pin, LOW);
   SPI.transfer(byte1);                                 
   SPI.transfer(byte2);
   digitalWrite(CS_pin, HIGH);
}

void TEC_DAC_load() {                                    // Loads data to LTC1658 14-bit DAC (laser TEC) through SPI
  unsigned int value = Serial.parseInt();                // Parses an int from the serial input
  value = value << 2;                                    // Converts a 32-bit int to 14 bit
  byte byte1 = (value >> 8);
  byte byte2 = (value & 0xff);
  digitalWrite(CS_DAC_TEC, LOW);
  SPI.transfer(byte1);
  SPI.transfer(byte2);
  digitalWrite(CS_DAC_TEC, HIGH);
  Serial.print("D DAC word: ");
  Serial.print(byte1, BIN);
  Serial.println(byte2, BIN);
}

void TEC_DAC_load(unsigned int value) {                  // Loads data to LTC1658 14-bit DAC (laser TEC) through SPI, takes Unsigned int value to write
  value = value << 2;  
  byte byte1 = (value >> 8);
  byte byte2 = (value & 0xff);
  digitalWrite(CS_DAC_TEC, LOW);
  SPI.transfer(byte1);
  SPI.transfer(byte2);
  digitalWrite(CS_DAC_TEC, HIGH);
  // Serial.print("D DAC word: ");
  // Serial.print(byte1, BIN);
  // Serial.println(byte2, BIN);
}


void ADF4158_Reg_Write() {                               // Writes an arbitrary PLL register
  unsigned int value1 = Serial.parseInt();               // Parses an int from the serial input
  digitalWrite(CS_ADF4158, LOW);
  delayMicroseconds(1);
  SPI.transfer(((value1 >> 24)& 0xff), SPI_CONTINUE);    // Splits the 32-bit int into 4 bytes
  SPI.transfer(((value1 >> 16)& 0xff), SPI_CONTINUE);
  SPI.transfer(((value1 >> 8)& 0xff), SPI_CONTINUE);
  SPI.transfer((value1& 0xff), SPI_CONTINUE);
  digitalWrite(CS_ADF4158, HIGH);
}


void ADF4158_Write(int value1) {                         // Writes one PLL register, takes int value as input
  digitalWrite(CS_ADF4158, LOW);
  delayMicroseconds(1);
  SPI.transfer(((value1 >> 24)& 0xff), SPI_CONTINUE);    // Splits the 32-bit int into 4 bytes
  SPI.transfer(((value1 >> 16)& 0xff), SPI_CONTINUE);
  SPI.transfer(((value1 >> 8)& 0xff), SPI_CONTINUE);
  SPI.transfer((value1& 0xff), SPI_CONTINUE);
  digitalWrite(CS_ADF4158, HIGH);
}

// CR: I found this function sets the RF synthesizer to 4.596301446 GHz exactly with a 10 MHz reference, with ramp mode activated.
void ADF4158_Set_CPT() {        // Sets PLL values to show CPT signal
  ADF4158_Write(0x7);           // R7: Delay disabled
  ADF4158_Write(0x800006);      // R6 - Ramp 2: Setting the number of steps to 0.
  ADF4158_Write(0x3E86);        // R6 - Ramp 1: Setting the number of steps to 2 000.
  ADF4158_Write(0x800005);      // R5 - Ramp 2: Disable the deviation.
  ADF4158_Write(0x1002A5);      // R5 - Ramp 1: Setting the deviation to "84" and offset to "2".
  ADF4158_Write(0x783204);      // R4: Set the clock divider mode to "ramp divider" and the divider value to 100.
  ADF4158_Write(0x43);          // R3: Set the ramp to continuous sawtooth.
  ADF4158_Write(0x40800A);      // R2: i charge pump (cp) set to 0.35mA /cyrus (CR: Set current setting to 0.31, r-counter divide ratio to 1 and clock divider to 1.)
  ADF4158_Write(0x1280001);     // R1: PRESCEDENT FFF8001 (CR: This register sets the LSb of the FRAC value)
  ADF4158_Write(0xF8E5D0A8);    // R0: pll setting= Muxout ramp Status on 0xF8E5D0A8 (CR: Set the MSb of the FRAC value and INT value)
}
// From the comments the "precedent" values were:
// R1: 0xFFF8001
// R0: 0xF8E5D0A8 (no change)
// This would set the frequency to 4.5963037106 GHz
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

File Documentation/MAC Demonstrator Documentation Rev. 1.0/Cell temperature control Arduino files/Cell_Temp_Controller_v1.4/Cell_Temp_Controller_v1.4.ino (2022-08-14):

#include <SPI.h>
#include <PID_v1.h>

const int CS_Cell_Temp_ADC = 10;
const int CS_Cell_Temp_DAC = 6;

double Input, Output;
double Kp=2, Ki=1, Kd=0, Setpoint= 28750;// Initial parameters Setpoint= 28750

PID myPID(&Input, &Output, &Setpoint, Kp, Ki, Kd, DIRECT);

void setup() {
  pinMode(CS_Cell_Temp_ADC, OUTPUT);
  pinMode(CS_Cell_Temp_DAC, OUTPUT);
  digitalWrite(CS_Cell_Temp_ADC, HIGH);
  digitalWrite(CS_Cell_Temp_DAC, HIGH);
  Serial.begin(9600);
  SPI.begin();
  myPID.SetMode(AUTOMATIC);
  myPID.SetOutputLimits(0x0, 0x1f40);

  //SPI.setClockDivider(SPI_CLOCK_DIV128); // Lower the SPI transmision speed

}

void loop() {
  Input = Cell_Temp_Read();
  myPID.Compute();
  Serial.println(Input);
  //Serial.println((int) Output);
  Cell_Temp_Write((int) Output);
  delay(100);
}

double Cell_Temp_Read(){
  digitalWrite(CS_Cell_Temp_ADC, LOW);
  unsigned int a = SPI.transfer(0x0);
  unsigned int b = SPI.transfer(0x0);
  digitalWrite(CS_Cell_Temp_ADC, HIGH);
  
  unsigned int adc_value = ((a << 8) | b);
  double Weatstone_V = (((double) adc_value / 32767) - 1) * 1.25;
  
  return (double)(((0.5-(Weatstone_V/1.25))/((0.5+Weatstone_V/1.25)))*10000);
}

void Cell_Temp_Write(int correction){
  byte a = (unsigned int) correction >> 8;
  byte b = (unsigned int) correction & 0xff;
  digitalWrite(CS_Cell_Temp_DAC, LOW);
  SPI.transfer(a);
  SPI.transfer(b);
  digitalWrite(CS_Cell_Temp_DAC, HIGH);
}  

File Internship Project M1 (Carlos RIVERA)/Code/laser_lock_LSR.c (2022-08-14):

/* README
 *
 * You may want to pay attention to the variables tags with "LOOK AT ME"
 *  test
 */



// classic lib
#include <stdio.h>
#include <unistd.h>
#include <sys/types.h>
#include <sys/stat.h>
#include <sys/ioctl.h>
#include <fcntl.h>
#include <math.h>
#include <time.h>
#include <sys/time.h>
#include <fftw3.h>
#include <string.h>
#include <signal.h> // to catch Ctrl + C from keyboard and close socket

//udp client
#include <sys/socket.h>
#include <netinet/in.h>
#include <arpa/inet.h>
#include <netdb.h>
#include <errno.h>
#include <stdlib.h>
#define BUF_SIZE 60

// DAC driver
#include <axi_to_dac_conf.h>

#define ELEMENT_SIZE 2048
#define N ELEMENT_SIZE

// LOOK AT ME
#define DAC_ELEMENT_SIZE 16384
// This variable define the number of level of the DAC.
// This is valable for a 14-bits DAC (2**14 = 16384)
// You may want to change this if your DACs are differents


// PID
// LOOK AT ME
#define Ts 0.08
// Ts is the sample time of the wavelength-meter
// If you look in Wavelength.exe on your w10 PC (shame on you), you will see somewhere "sleep(TIME_CONSTANT)"
// Ts must be the same than TIME_CONSTANT
// DO NOT CHANGE Ts WITHOUT CHANGE TIME_CONSTANT
// TODO: Ts isn't use anymore



/************************************/
/************ LOOK AT ME ************/
/************************************/

// Uncomment this to use the PID implemented in this code.
// Otherwise the DACs output is only the error signal.
#define USE_REDPITAYA_PID

/************************************/
/************************************/
/************************************/





//udp
int sock;
struct sockaddr_in server_addr;
struct hostent *host;
char send_data[1024];
//char recv_data[BUF_SIZE];
double recv_data;
double recv_lambda;
int bytes_read;
socklen_t addr_len;
//eudp

struct timeval start,stop;
double elapsed_time;
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

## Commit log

2022-06-08 Added comments on registers and flowchart until #6
2022-07-05 mac arduino final version clock 1
2022-07-26 Final status at report v1.0
    [scope_2.csv]
2022-07-28 Removed TEC serial prints
2022-08-14 Clean up of git content
    [10 MHz Buffer v1.0.brd, 10 MHz Buffer v1.0.sch, Atomic clock test board v1.1.brd, Atomic clock test board v1.1.sch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]

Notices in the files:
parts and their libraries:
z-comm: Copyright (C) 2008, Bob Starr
